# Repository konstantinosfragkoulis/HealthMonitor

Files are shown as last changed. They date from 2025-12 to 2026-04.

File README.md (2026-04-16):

# HealthMonitor 

Bare metal wearable for real-time Electrocardiogram (ECG), Seismocardiogram (SCG), and respiratory rate extraction.

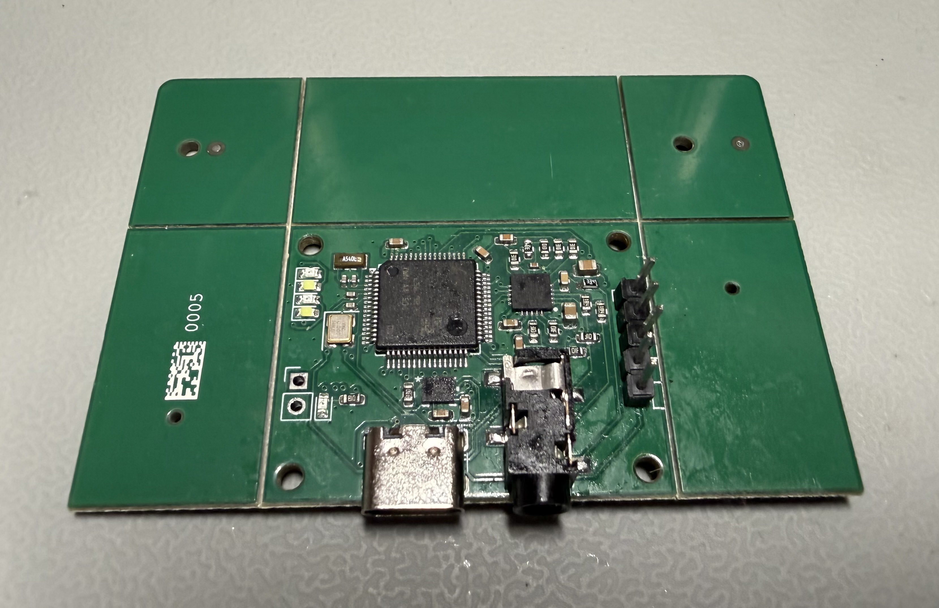
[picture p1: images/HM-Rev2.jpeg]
Health Monitor Rev2 PCB


**Core Stack:** STM32U5 (Cortex-M33) | ST1VAFE6AX (6-axis IMU) | AD8232 (ECG AFE)

## Architecture & DSP
To guarantee precise timing, the firmware relies entirely on hardware synchronization. The IMU's data-ready external interrupt triggers a simultaneous DMA transfer for both the SPI bus (IMU) and the ADC (ECG). This locks both data streams to a 480 Hz sample rate, eliminating software polling jitter.

The main loop runs three independent DSP pipelines on-device:

* **ECG (Pan-Tompkins++):** Bandpass -> derivative -> squaring -> flattop smoothing -> MWI. Uses adaptive thresholding with search-back for real-time R-peak detection [1].
* **SCG (Template Matching NCC):** Accel Z-axis (dorso-ventral) filtered at 7-30 Hz. Bootstraps a heartbeat template during the first 10s via a 4th-power envelope and pairwise NCC [2]. Runs a sliding normalized cross-correlation against the template for continuous AO detection. The template is double-buffered and refreshed every 60s.
* **Respiratory Rate:** Accel Z-axis LPF -> decimated 48:1 (to 10 Hz) -> bandpass 0.1-0.6 Hz. Fed into a 30-second autocorrelation window, outputting a new respiratory rate every 5 seconds.

HRV metrics (RMSSD, SDNN, pNN50, SD1, SD2) are calculated independently for both the ECG and SCG streams over a 60 second sliding window based on Task Force standards [3,4]. ECG and SCG reports are synchronized as the ECG trigger drives both computations simultaneously. Data is streamed to a host via a USB Virtual COM Port with CRC-32 integrity.

## Project Structure
* `/hardware/HM-Rev1`: First spin. **See `ERRATA.md`** (known routing/schematic flaw with the AD8232).
* `/hardware/HM-Rev2`: Fixed AD8232 layout, added USB-C, placed components on the bottom layer.
* `/fw`: STM32CubeIDE project, bare-metal C source, DSP logic, and TinyUSB stack.
* `/software`: Python telemetry parser and plotter.

## Roadmap
- [x] Hardware validation.
- [x] Synchronized IMU + ECG DMA capture.
- [x] ECG R-peak detection (Pan-Tompkins++).
- [x] SCG heartbeat detection (Template Matching NCC).
- [x] Real-time respiratory rate from chest-wall accelerometry.
- [x] On-device HRV metrics calculation.
- [x] USB CDC telemetry via TinyUSB.
- [x] SCG vs ECG HRV validation.
- [ ] Improve SCG RMSSD agreement
- [ ] Multi-axis respiratory fusion (PCA + gyro).

## SCG vs ECG HRV Validation

To validate the SCG pipeline, both streams are recorded simultaneously and HRV metrics are compared using Bland-Altman analysis, Pearson correlation, and ICC(2,1). Results from a 30 minute resting session (single subject, n=57 paired reports after 4 outliers removed via 3xIQR on RMSSD):

| Metric | Bias | 95% LOA | r | ICC(2,1) |
|--------|------|---------|---|----------|
| SDNN | -2.0 ms | [-6.0, +1.9] | 0.988 | 0.961 |
| SD2 | -0.9 ms | [-3.6, +1.9] | 0.996 | 0.994 |
| RMSSD | -6.3 ms | [-16.2, +3.5] | 0.378 | 0.175 |

SDNN and SD2 show excellent agreement. RMSSD underestimates ECG systematically. The SCG pipeline captures long term variability accurately but doesn't perform well with beat-to-beat variations.

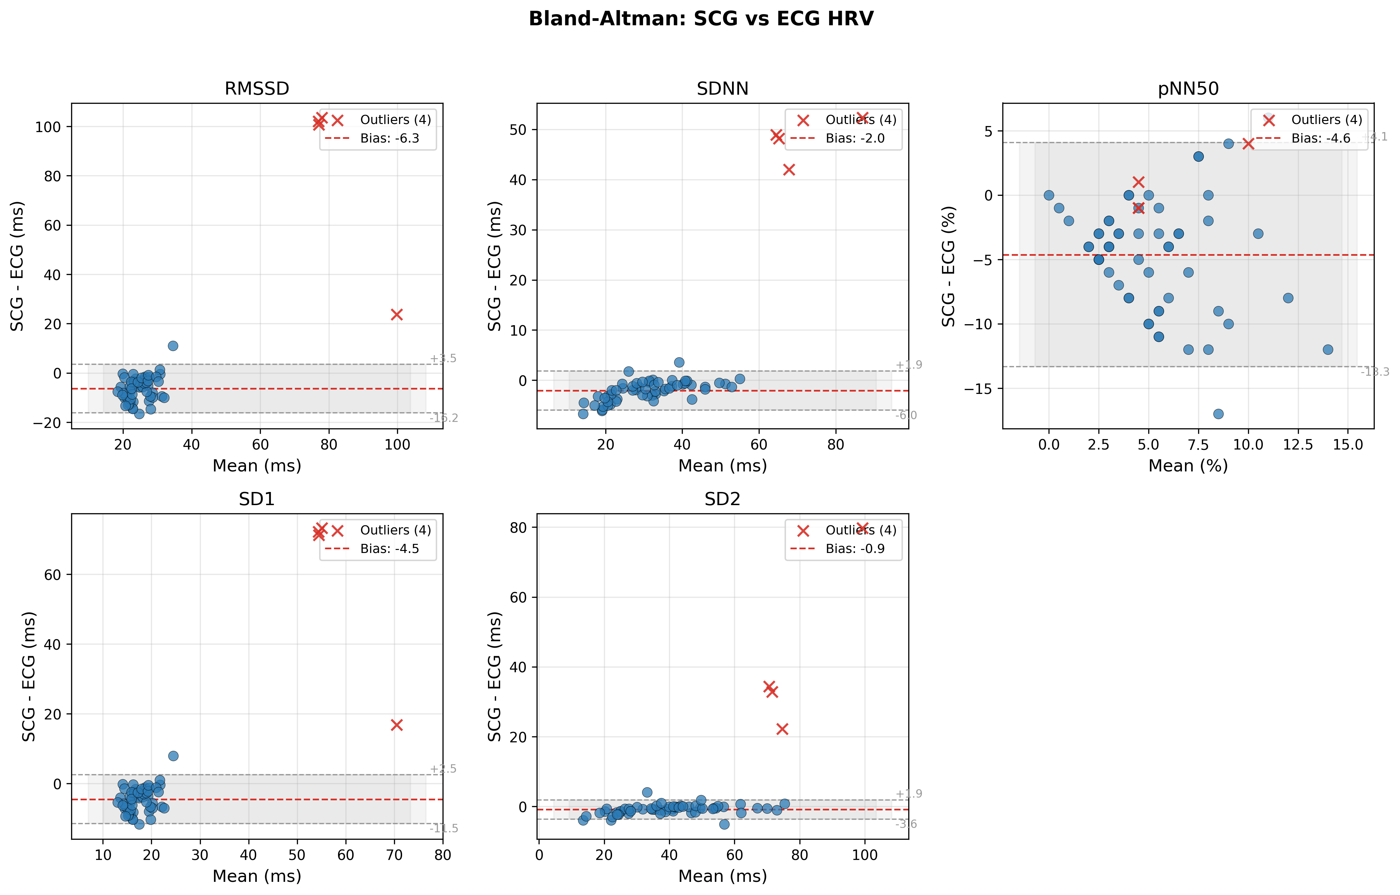
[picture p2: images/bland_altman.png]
Bland-Altman: SCG vs ECG HRV


The validation script reports both unfiltered and filtered results.
Run `python software/analyze.py <session_dir>` to produce the table and plots with data saved from the `software/monitor.py` script.

## Build Instructions
Compiled with **STM32CubeIDE**.
1. `git clone https://github.com/konstantinosfragkoulis/HealthMonitor.git`
2. Open STM32CubeIDE > `File > STM32 Project Create/Import > Import STM32 Project > STM32CubeMX/STM32CubeIDE Project`.
3. Point to the `/fw` directory.
4. Build (Release/Debug) and flash via ST-Link.

## Host Telemetry
The STM32 streams binary packets over USB CDC. Use the included Python script to plot sensor data in real time.

```bash
cd software
pip install pyserial numpy matplotlib # You might want to use a virtual environment for this

# Auto detect port
python monitor.py

# Manually select port
python monitor.py COM3         # Windows
python monitor.py /dev/ttyACM0 # Linux
```

## References
- USB stack powered by the open-source [TinyUSB](https://github.com/hathach/tinyusb) library (MIT License).

[1] M. N. Imtiaz and N. Khan, "Pan-Tompkins++: A Robust Approach to Detect R-peaks in ECG Signals," in *Proc. IEEE Int. Conf. Bioinformatics and Biomedicine (BIBM) Workshops*, 2022. [Online]. Available: https://arxiv.org/abs/2211.03171

[2] S. Parlato, J. Centracchio, D. Esposito, P. Bifulco, and E. Andreozzi, "Fully automated template matching method for ECG-free heartbeat detection in cardiomechanical signals," *Physical and Engineering Sciences in Medicine*, vol. 48, pp. 649-664, 2025.

[3] Task Force of the European Society of Cardiology and the North American Society of Pacing and Electrophysiology, "Heart rate variability: standards of measurement, physiological interpretation and clinical use," *Circulation*, vol. 93, pp. 1043-1065, 1996.

[4] F. Shaffer and J. P. Ginsberg, "An Overview of Heart Rate Variability Metrics and Norms," *Frontiers in Public Health*, vol. 5, 258, 2017.

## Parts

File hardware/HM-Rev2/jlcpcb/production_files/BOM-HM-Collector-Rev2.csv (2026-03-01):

Comment | Designator | Footprint | LCSC | Quantity
100k | R13 | R_0603_1608Metric | C25803 | 1
100n | C1,C12,C15,C22,C23,C29,C30,C31,C32,C33,C4,C5,C6,C8 | C_0603_1608Metric | C14663 | 14
10M | R10,R3,R4,R5,R9 | R_0603_1608Metric | C7250 | 5
10k | R1,R19,R2,R22 | R_0603_1608Metric | C25804 | 4
10u | C34,C35,C7,C9 | C_0805_2012Metric | C440198 | 4
12p | C16,C17 | C_0402_1005Metric | C1547 | 2
180k | R6,R7 | R_0603_1608Metric | C22827 | 2
18p | C18,C19 | C_0402_1005Metric | C1549 | 2
1M | R11,R12,R15,R20,R21 | R_0603_1608Metric | C22935 | 5
1k | R28,R29,R30,R31,R32 | R_0603_1608Metric | C21190 | 5
1n | C25 | C_0603_1608Metric | C1588 | 1
1u | C13,C14,C2,C20,C21,C3 | C_0603_1608Metric | C15849 | 6
2.2u | C10,C11 | C_0603_1608Metric | C23630 | 2
2.7n | C27 | C_0603_1608Metric | C1609 | 1
33 | R16,R17,R18,R23,R24,R25 | R_0603_1608Metric | C23140 | 6
4.7u | C24,C28 | C_0805_2012Metric | C1779 | 2
5.1k | R26,R27 | R_0603_1608Metric | C23186 | 2
6.8n | C26 | C_0402_1005Metric | C1542 | 1
AD8232ACPZ-R7 | IC2 | QFN50P400X400X80-21N-D | C43216 | 1
Crystal | Y2 | Crystal_SMD_3215-2Pin_3.2x1.5mm | C32346 | 1
Crystal_GND24 | Y1 | Crystal_SMD_3225-4Pin_3.2x2.5mm | C13738 | 1
D | D1,D2 | D_SOD-123 | C8598 | 2
LED | D3,D5,D7 | LED_0603_1608Metric | C2286 | 3
LED | D4,D6 | LED_0603_1608Metric | C2290 | 2
ST1VAFE6AXTR | U2 | LGA-14L_STM | C23536654 | 1
STM32U595RJTxQ | U1 | LQFP-64_10x10mm_P0.5mm | C27526235 | 1
TPS7A2028PDBVR | IC1,IC3 | SOT95P280X145-5N | C2862740 | 2
USB_C_Receptacle_USB2.0_16P | J3 | USB_C_Receptacle_GCT_USB4105-xx-A_16P_TopMnt_Horizontal | C709357 | 1

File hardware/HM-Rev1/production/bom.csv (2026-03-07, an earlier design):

Designator | Footprint | Quantity | Value | LCSC Part #
C1, C10, C11, C16, C18, C2, C20, C29, C3, C30, C35, C36, C37, C4, C5, C6, C7, C8, C9 | 0603 | 19 | 100nF
C12, C15 | 0805 | 2 | 10uF
C13, C14 | 0603 | 2 | 2.2uF
C17, C19, C25, C26, C27, C28 | 0603 | 6 | 1uF
C21, C22 | 0402 | 2 | 8pF
C23, C24 | 0402 | 2 | 6pF
C31 | 0805 | 1 | 4.7uF
C32 | 0603 | 1 | 1nF
C33 | 0402 | 1 | 6.8nF
C34 | 0402 | 1 | 2.7nF
D1, D2, D3, D4 | 0402 | 4 | LED
IC1, IC2 | SOT95P280X145-5N | 2 | TPS7A2028PDBVR
IC3 | QFN50P400X400X80-21N-D | 1 | AD8232ACPZ-R7
J1 | PinHeader_1x05_P2.54mm_Horizontal | 1 | Conn_01x05_Pin
J2 | SJ235813BSMTTR | 1 | SJ2-35813B-SMT-TR
L1 | 1008 | 1 | 2.2uH
R1, R2, R21, R22, R23, R24, R25, R26 | 0603 | 8 | 10kOhm
R10 | 0603 | 1 | 360kOhm
R11, R13, R15, R16, R17 | 0603 | 5 | 1MOhm
R12 | 0603 | 1 | 100kOhm
R14 | 0603 | 1 | 332kOhm
R18, R19, R20, R27, R28, R29 | 0402 | 6 | 33Ohm
R3, R4, R5, R8, R9 | 0603 | 5 | 10MOhm
R6, R7 | 0603 | 2 | 180kOhm
TP1, TP2 | PinHeader_1x01_P2.54mm_Vertical | 2 | TestPoint
U1 | LQFP-100_14x14mm_P0.5mm | 1 | STM32U5G9VJTxQ
U2 | LGA-14L_STM | 1 | ST1VAFE6AXTR
U3 | SOIC-8_5.3x5.3mm_P1.27mm | 1 | W25Q128JVS
Y1 | Crystal_SMD_3215-2Pin_3.2x1.5mm | 1 | 32.768kHz
Y2 | CX3225FB16000D0FZZH1 | 1 | CX3225FB16000D0FZZH1

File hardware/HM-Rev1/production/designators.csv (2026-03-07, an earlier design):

C1:1
C10:1
C11:1
C12:1
C13:1
C14:1
C15:1
C16:1
C17:1
C18:1
C19:1
C2:1
C20:1
C21:1
C22:1
C23:1
C24:1
C25:1
C26:1
C27:1
C28:1
C29:1
C3:1
C30:1
C31:1
C32:1
C33:1
C34:1
C35:1
C36:1
C37:1
C4:1
C5:1
C6:1
C7:1
C8:1
C9:1
D1:1
D2:1
D3:1
D4:1
IC1:1
IC2:1
IC3:1
J1:1
J2:1
JP1:1
L1:1
R1:1
R10:1
R11:1
R12:1
R13:1
R14:1
R15:1
R16:1
R17:1
R18:1
R19:1
R2:1
R20:1
R21:1
R22:1
R23:1
R24:1
R25:1
R26:1
R27:1
R28:1
R29:1
R3:1
R4:1
R5:1
R6:1
R7:1
R8:1
R9:1
TP1:1
TP2:1
U1:1
U2:1
U3:1
Y1:1
Y2:1

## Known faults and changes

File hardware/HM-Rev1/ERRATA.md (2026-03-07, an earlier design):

# HM-Rev1 Known Issues

**Note: This board was abandoned and never fully assembled**

## 1. AD8232 Incorrect Wiring
* One 4.7 uF capacitor is missing between IOUT and SW
* One resistor and one capacitor are wired incorrectly between REFIN and GND

This error was caught *before* testing the board, so the AD8232 was never tested. Most likely, the signal filtering would not have worked correctly. This is fixed in [HM-Rev2](../HM-Rev2).

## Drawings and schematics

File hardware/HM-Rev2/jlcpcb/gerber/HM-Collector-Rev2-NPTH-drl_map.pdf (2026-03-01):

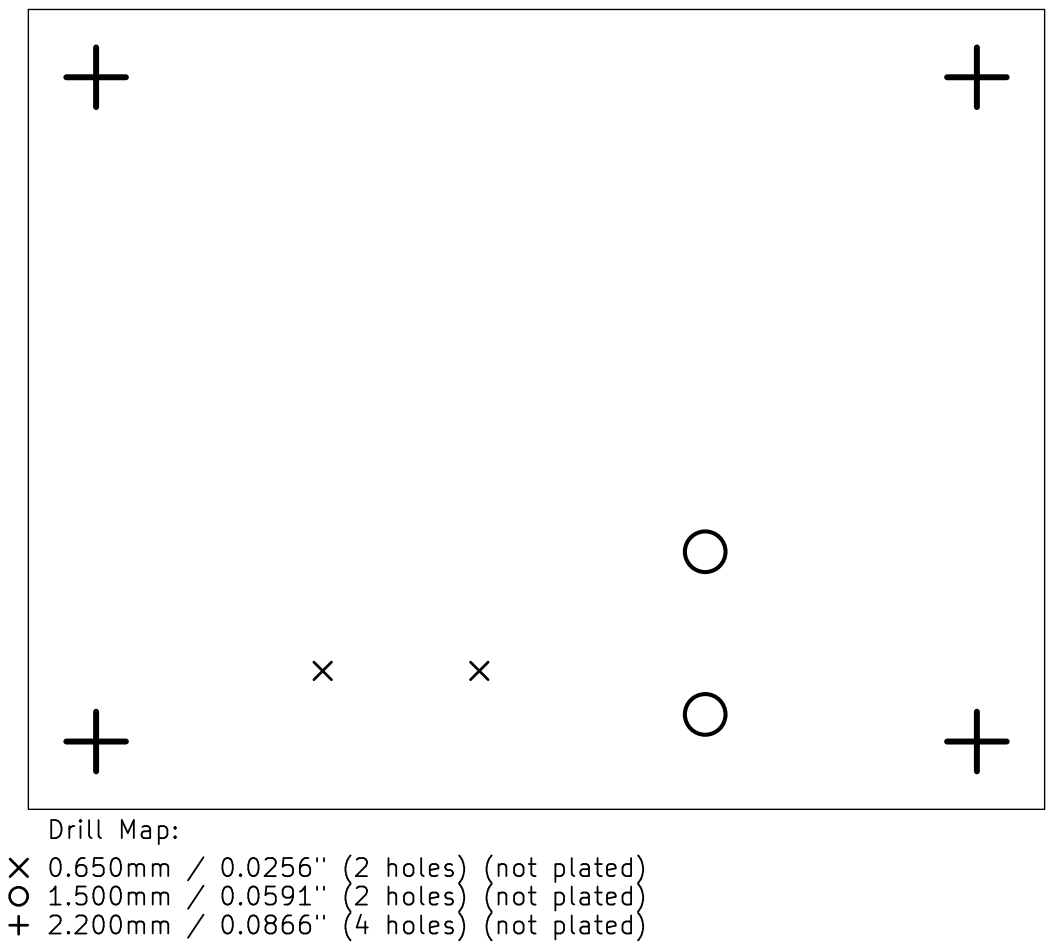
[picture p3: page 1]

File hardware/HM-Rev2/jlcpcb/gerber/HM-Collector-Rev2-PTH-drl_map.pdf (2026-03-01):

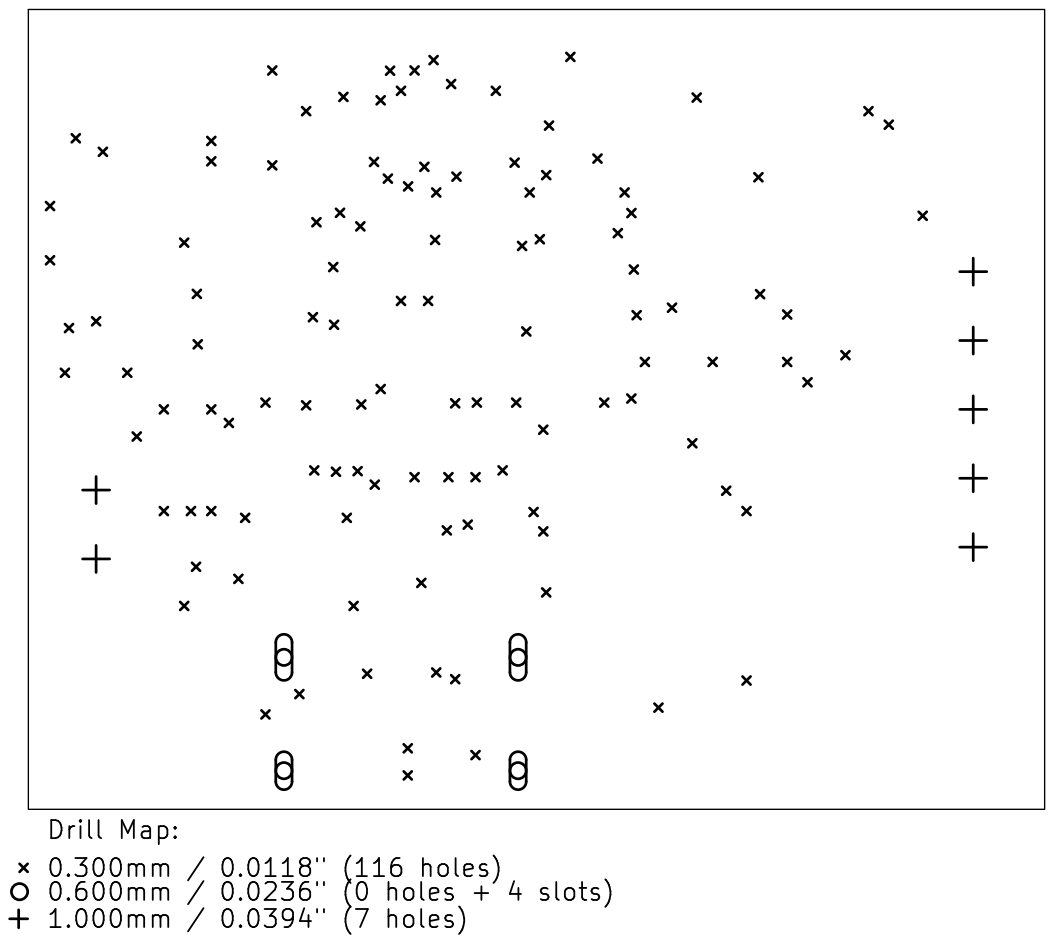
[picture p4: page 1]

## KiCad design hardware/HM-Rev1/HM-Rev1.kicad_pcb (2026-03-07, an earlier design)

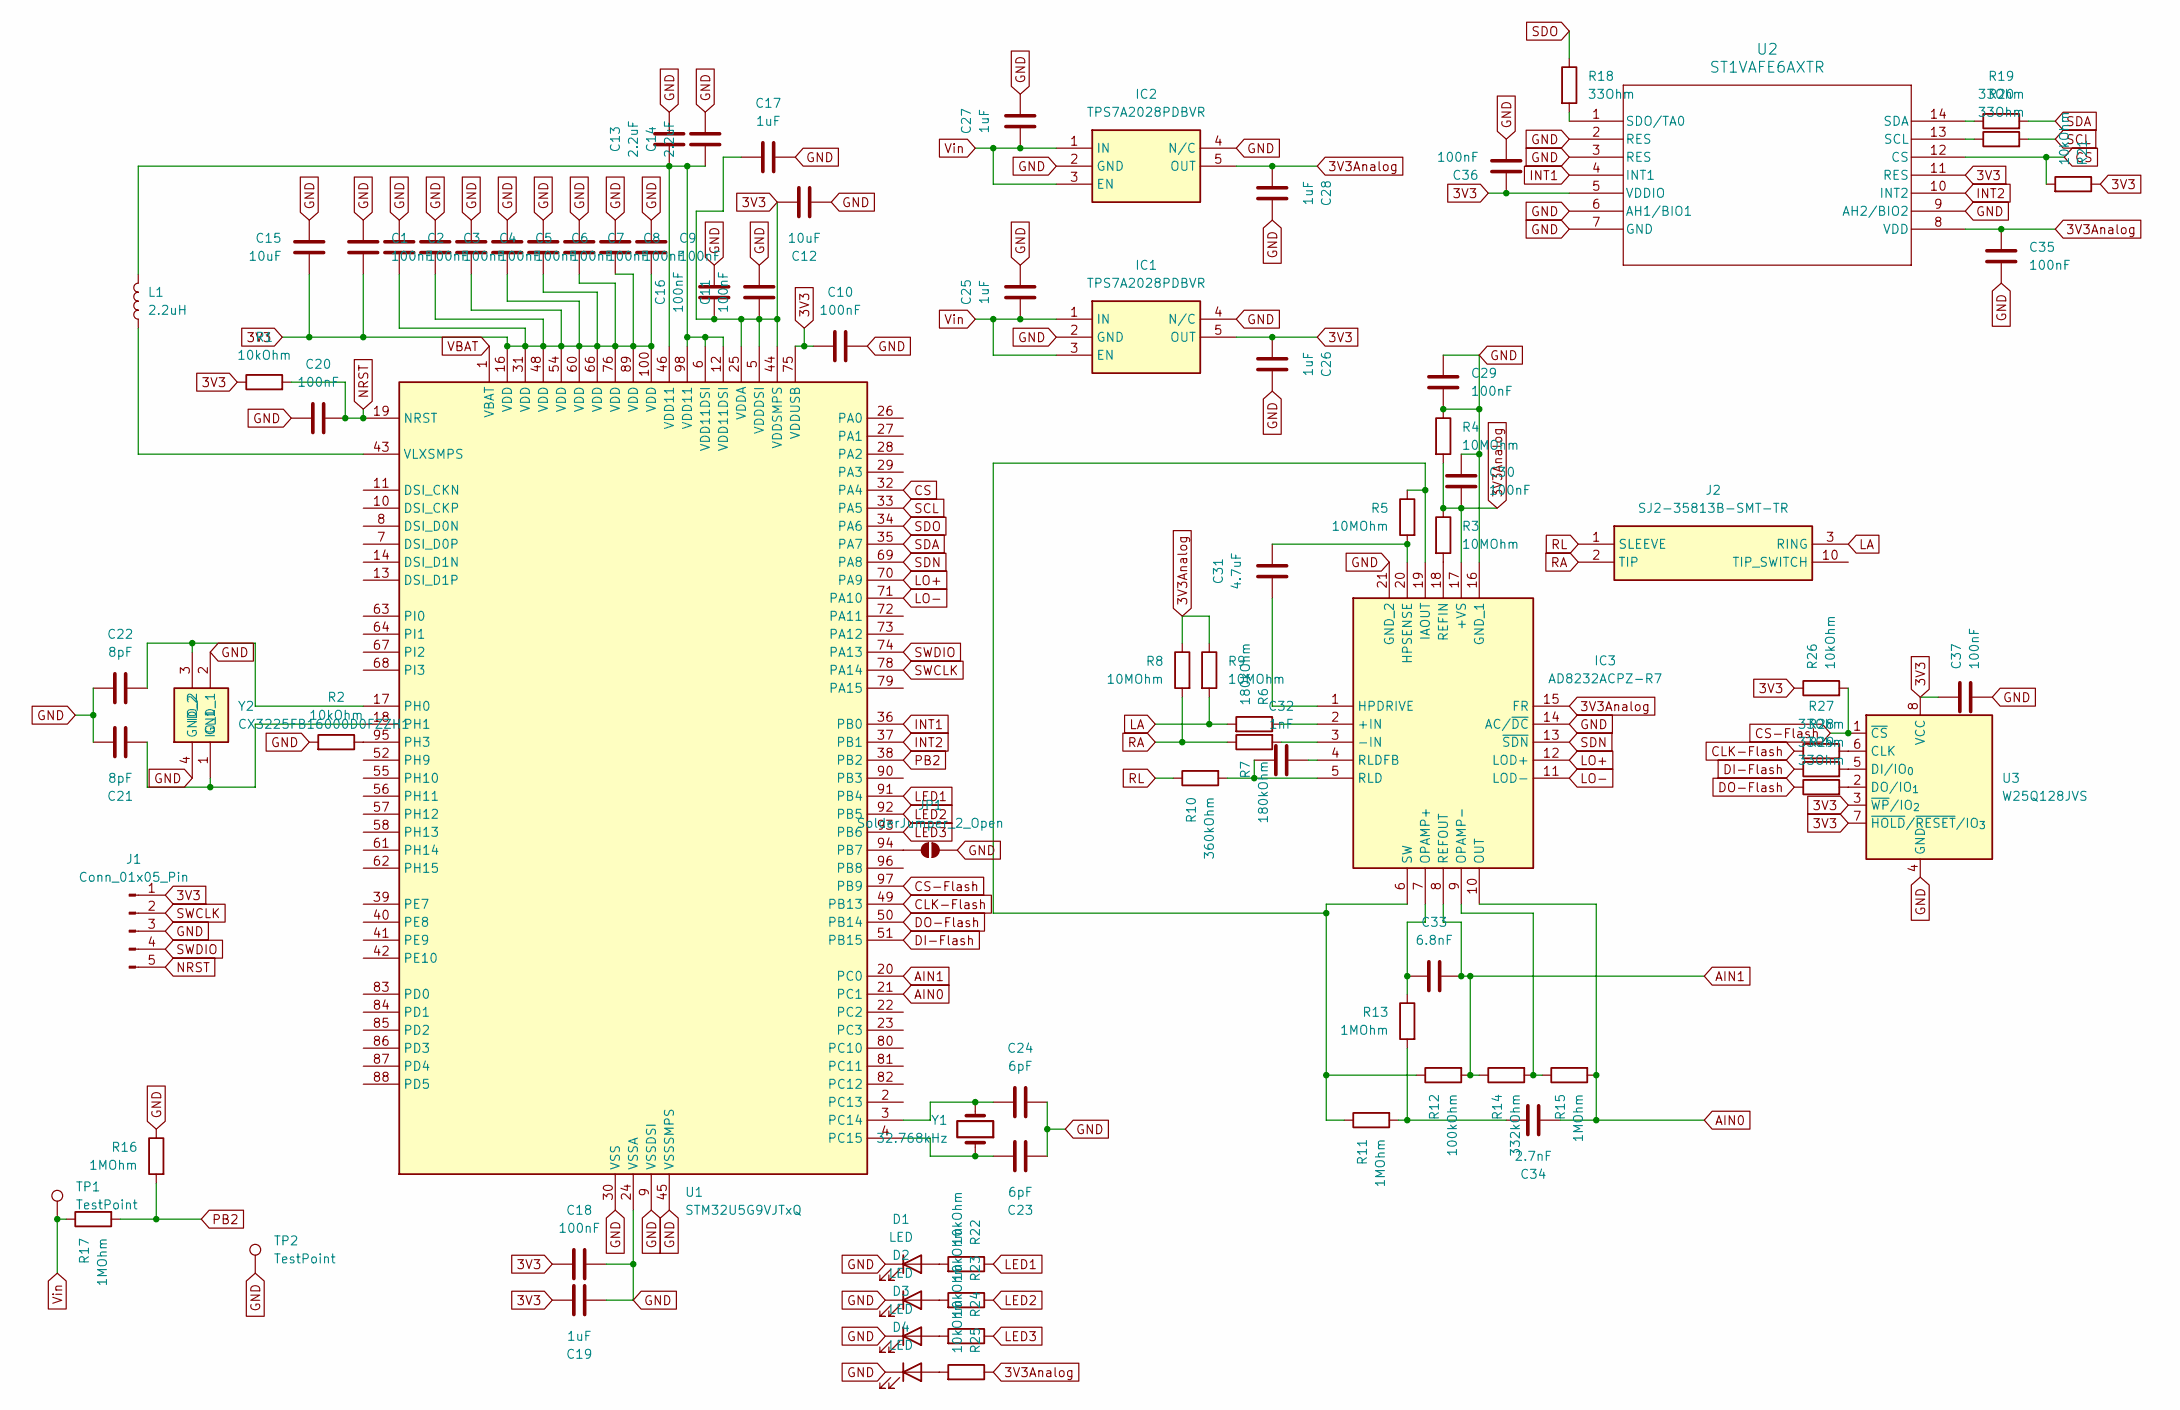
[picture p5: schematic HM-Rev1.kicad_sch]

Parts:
C1, C2, C3, C4, C5, C6, C7, C8, C9, C10, C11, C16, C18, C20, C29, C30, C35, C36, C37: 100nF; C_0603_1608Metric
C12, C15: 10uF; C_0805_2012Metric
C13, C14: 2.2uF; C_0603_1608Metric
C17, C19, C25, C26, C27, C28: 1uF; C_0603_1608Metric
C21, C22: 8pF; C_0402_1005Metric
C23, C24: 6pF; C_0402_1005Metric
C31: 4.7uF; C_0805_2012Metric
C32: 1nF; C_0603_1608Metric
C33: 6.8nF; C_0402_1005Metric
C34: 2.7nF; C_0402_1005Metric
D1, D2, D3, D4: LED; LED_0402_1005Metric_Pad0.77x0.64mm_HandSolder
IC1, IC2: TPS7A2028PDBVR; SOT95P280X145-5N; Mouser Part Number 595-TPS7A2028PDBVR
IC3: AD8232ACPZ-R7; QFN50P400X400X80-21N-D; Mouser Part Number 584-AD8232ACPZ-R7
J1: Conn_01x05_Pin; PinHeader_1x05_P2.54mm_Horizontal
J2: SJ2-35813B-SMT-TR; SJ235813BSMTTR; Mouser Part Number 490-SJ2-35813BSMT-TR
JP1: SolderJumper_2_Open; SolderJumper-2_P1.3mm_Open_Pad1.0x1.5mm
L1: 2.2uH; L_1008_2520Metric
R1, R2, R21, R22, R23, R24, R25, R26: 10kOhm; R_0603_1608Metric
R3, R4, R5, R8, R9: 10MOhm; R_0603_1608Metric
R6, R7: 180kOhm; R_0603_1608Metric
R10: 360kOhm; R_0603_1608Metric
R11, R13, R15, R16, R17: 1MOhm; R_0603_1608Metric
R12: 100kOhm; R_0603_1608Metric
R14: 332kOhm; R_0603_1608Metric
R18, R19, R20, R27, R28, R29: 33Ohm; R_0402_1005Metric
TP1, TP2: TestPoint; PinHeader_1x01_P2.54mm_Vertical
U1: STM32U5G9VJTxQ; LQFP-100_14x14mm_P0.5mm
U2: ST1VAFE6AXTR; LGA-14L_STM
U3: W25Q128JVS; SOIC-8_5.3x5.3mm_P1.27mm
Y1: 32.768kHz; Crystal_SMD_3215-2Pin_3.2x1.5mm
Y2: CX3225FB16000D0FZZH1; Manufacturer_Part_Number CX3225FB16000D0FZZH1

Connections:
3V3: C1.2, C2.2, C3.2, C4.2, C5.2, C6.2, C7.2, C8.2, C9.2, C10.1, C11.1, C12.1, C15.2, C16.1, C17.1, C18.2, C19.1, C26.1, C36.1, C37.1, IC1.5 (OUT), J1.1, R1.1, R21.1, R26.1, U1.5 (VDDDSI), U1.16 (VDD), U1.25 (VDDA), U1.31 (VDD), U1.44 (VDDSMPS), U1.48 (VDD), U1.54 (VDD), U1.60 (VDD), U1.66 (VDD), U1.75 (VDDUSB), U1.76 (VDD), U1.89 (VDD), U1.100 (VDD), U2.5 (VDDIO), U2.11 (RES), U3.3 (~WP/IO_{2}), U3.7 (~HOLD/~RESET/IO_{3}), U3.8 (VCC)
3V3Analog: C28.1, C30.1, C35.1, IC2.5 (OUT), IC3.15 (FR), IC3.17 (+VS), R3.1, R4.2, R8.1, R9.1, R25.1, U2.8 (VDD)
AIN0: C34.2, IC3.10 (OUT), R15.2, U1.21 (PC1)
AIN1: C33.1, IC3.8 (REFOUT), R12.2, R14.1, U1.20 (PC0)
CLK-Flash: R27.1, U1.49 (PB13)
CS: R21.2, U1.32 (PA4), U2.12 (CS)
CS-Flash: R26.2, U1.97 (PB9), U3.1 (~CS)
DI-Flash: R28.1, U1.51 (PB15)
DO-Flash: R29.1, U1.50 (PB14)
GND: C1.1, C2.1, C3.1, C4.1, C5.1, C6.1, C7.1, C8.1, C9.1, C10.2, C11.2, C12.2, C13.2, C14.2, C15.1, C16.2, C17.2, C18.1, C19.2, C20.1, C21.1, C22.2, C23.2, C24.1, C25.2, C26.2, C27.2, C28.2, C29.1, C29.2, C30.2, C35.2, C36.2, C37.2, D1.1 (K), D2.1 (K), D3.1 (K), D4.1 (K), IC1.2 (GND), IC1.4 (N/C), IC2.2 (GND), IC2.4 (N/C), IC3.14 (AC/~DC), IC3.16 (GND_1), IC3.21 (GND_2), J1.3, JP1.2 (B), R2.2, R4.1, R16.1, TP2.1, U1.9 (VSSDSI), U1.15 (VSSDSI), U1.24 (VSSA), U1.30 (VSS), U1.45 (VSSSMPS), U1.47 (VSS), U1.53 (VSS), U1.59 (VSS), U1.65 (VSS), U1.77 (VSS), U1.99 (VSS), U2.2 (RES), U2.3 (RES), U2.6 (AH1/BIO1), U2.7 (GND), U2.9 (AH2/BIO2), U3.4 (GND), Y2.2 (GND_1), Y2.4 (GND_2)
INT1: U1.36 (PB0), U2.4 (INT1)
INT2: U1.37 (PB1), U2.10 (INT2)
LA: J2.3 (RING), R6.2, R9.2
LED1: R22.1, U1.91 (PB4)
LED2: R23.1, U1.92 (PB5)
LED3: R24.1, U1.93 (PB6)
LO+: IC3.12 (LOD+), U1.70 (PA9)
LO-: IC3.11 (LOD-), U1.71 (PA10)
NRST: C20.2, J1.5, R1.2, U1.19 (NRST)
unnamed: C13.1, C14.1, L1.2, U1.6 (VDD11DSI), U1.12 (VDD11DSI), U1.46 (VDD11), U1.98 (VDD11)
unnamed: C34.1, R11.2, R13.2
unnamed: D1.2 (A), R22.2
unnamed: D2.2 (A), R23.2
unnamed: D3.2 (A), R24.2
unnamed: D4.2 (A), R25.2
unnamed: IC3.2 (+IN), R6.1
unnamed: IC3.3 (-IN), R7.2
unnamed: C31.1, IC3.1 (HPDRIVE)
unnamed: C31.2, IC3.20 (HPSENSE), R5.2
unnamed: IC3.6 (SW), IC3.19 (IAOUT), R5.1, R11.1, R12.1
unnamed: C33.2, IC3.7 (OPAMP+), R13.1
unnamed: IC3.9 (OPAMP-), R14.2, R15.1
unnamed: IC3.18 (REFIN), R3.2
unnamed: C32.2, IC3.5 (RLD), R10.2
unnamed: C32.1, IC3.4 (RLDFB)
unnamed: JP1.1 (A), U1.94 (PB7)
unnamed: C24.2, U1.3 (PC14), Y1.2
unnamed: C23.1, U1.4 (PC15), Y1.1
unnamed: C22.1, U1.17 (PH0), Y2.3 (IO_2)
unnamed: C21.2, U1.18 (PH1), Y2.1 (IO_1)
unnamed: R2.1, U1.95 (PH3)
unnamed: L1.1, U1.43 (VLXSMPS)
unnamed: R20.1, U2.13 (SCL)
unnamed: R19.1, U2.14 (SDA)
unnamed: R18.2, U2.1 (SDO/TA0)
unnamed: R27.2, U3.6 (CLK)
unnamed: R28.2, U3.5 (DI/IO_{0})
unnamed: R29.2, U3.2 (DO/IO_{1})
PB2: R16.2, R17.2, U1.38 (PB2)
RA: J2.2 (TIP), R7.1, R8.2
RL: J2.1 (SLEEVE), R10.1
SCL: R20.2, U1.33 (PA5)
SDA: R19.2, U1.35 (PA7)
SDN: IC3.13 (~SDN), U1.69 (PA8)
SDO: R18.1, U1.34 (PA6)
SWCLK: J1.2, U1.78 (PA14)
SWDIO: J1.4, U1.74 (PA13)
VBAT: U1.1 (VBAT)
Vin: C25.1, C27.1, IC1.1 (IN), IC1.3 (EN), IC2.1 (IN), IC2.3 (EN), R17.1, TP1.1

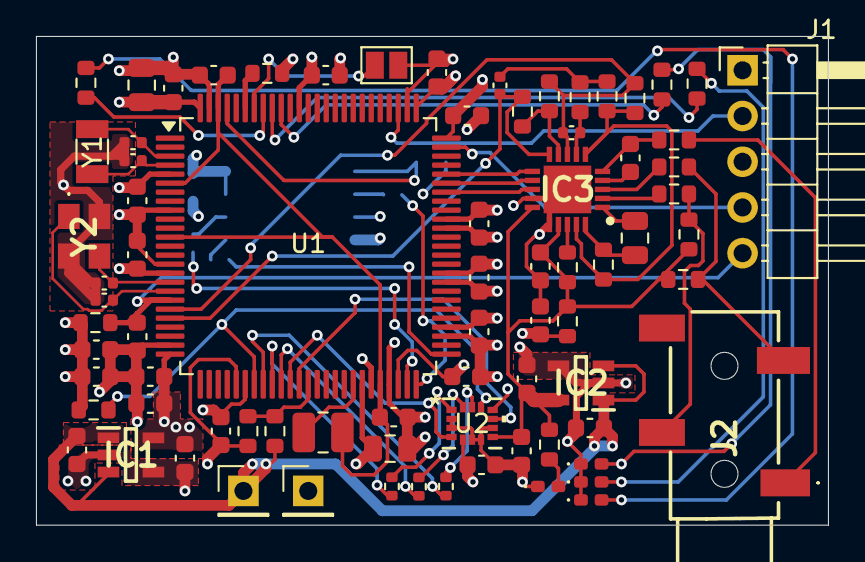
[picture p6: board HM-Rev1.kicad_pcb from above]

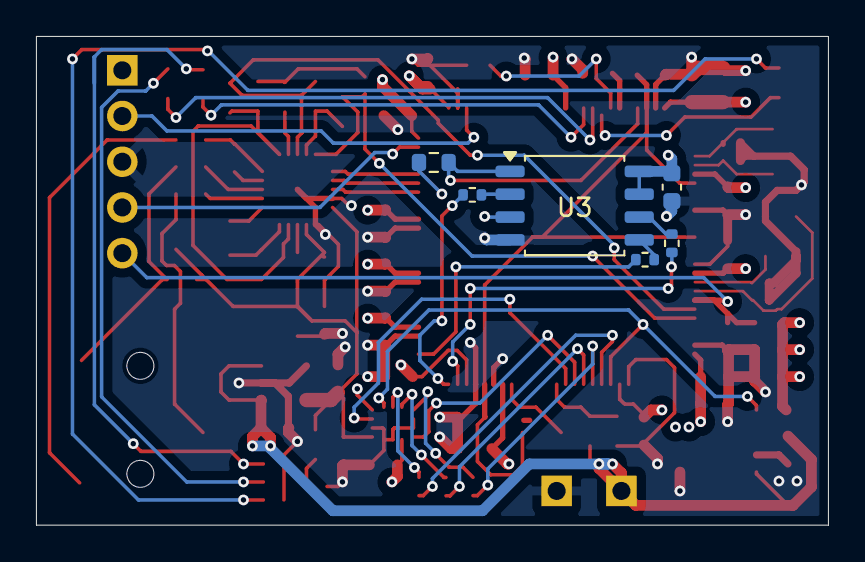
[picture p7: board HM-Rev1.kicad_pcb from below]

Board: 4 copper layers, 44.0 x 27.2 mm, 84 parts (6 on the bottom side), 58 nets.

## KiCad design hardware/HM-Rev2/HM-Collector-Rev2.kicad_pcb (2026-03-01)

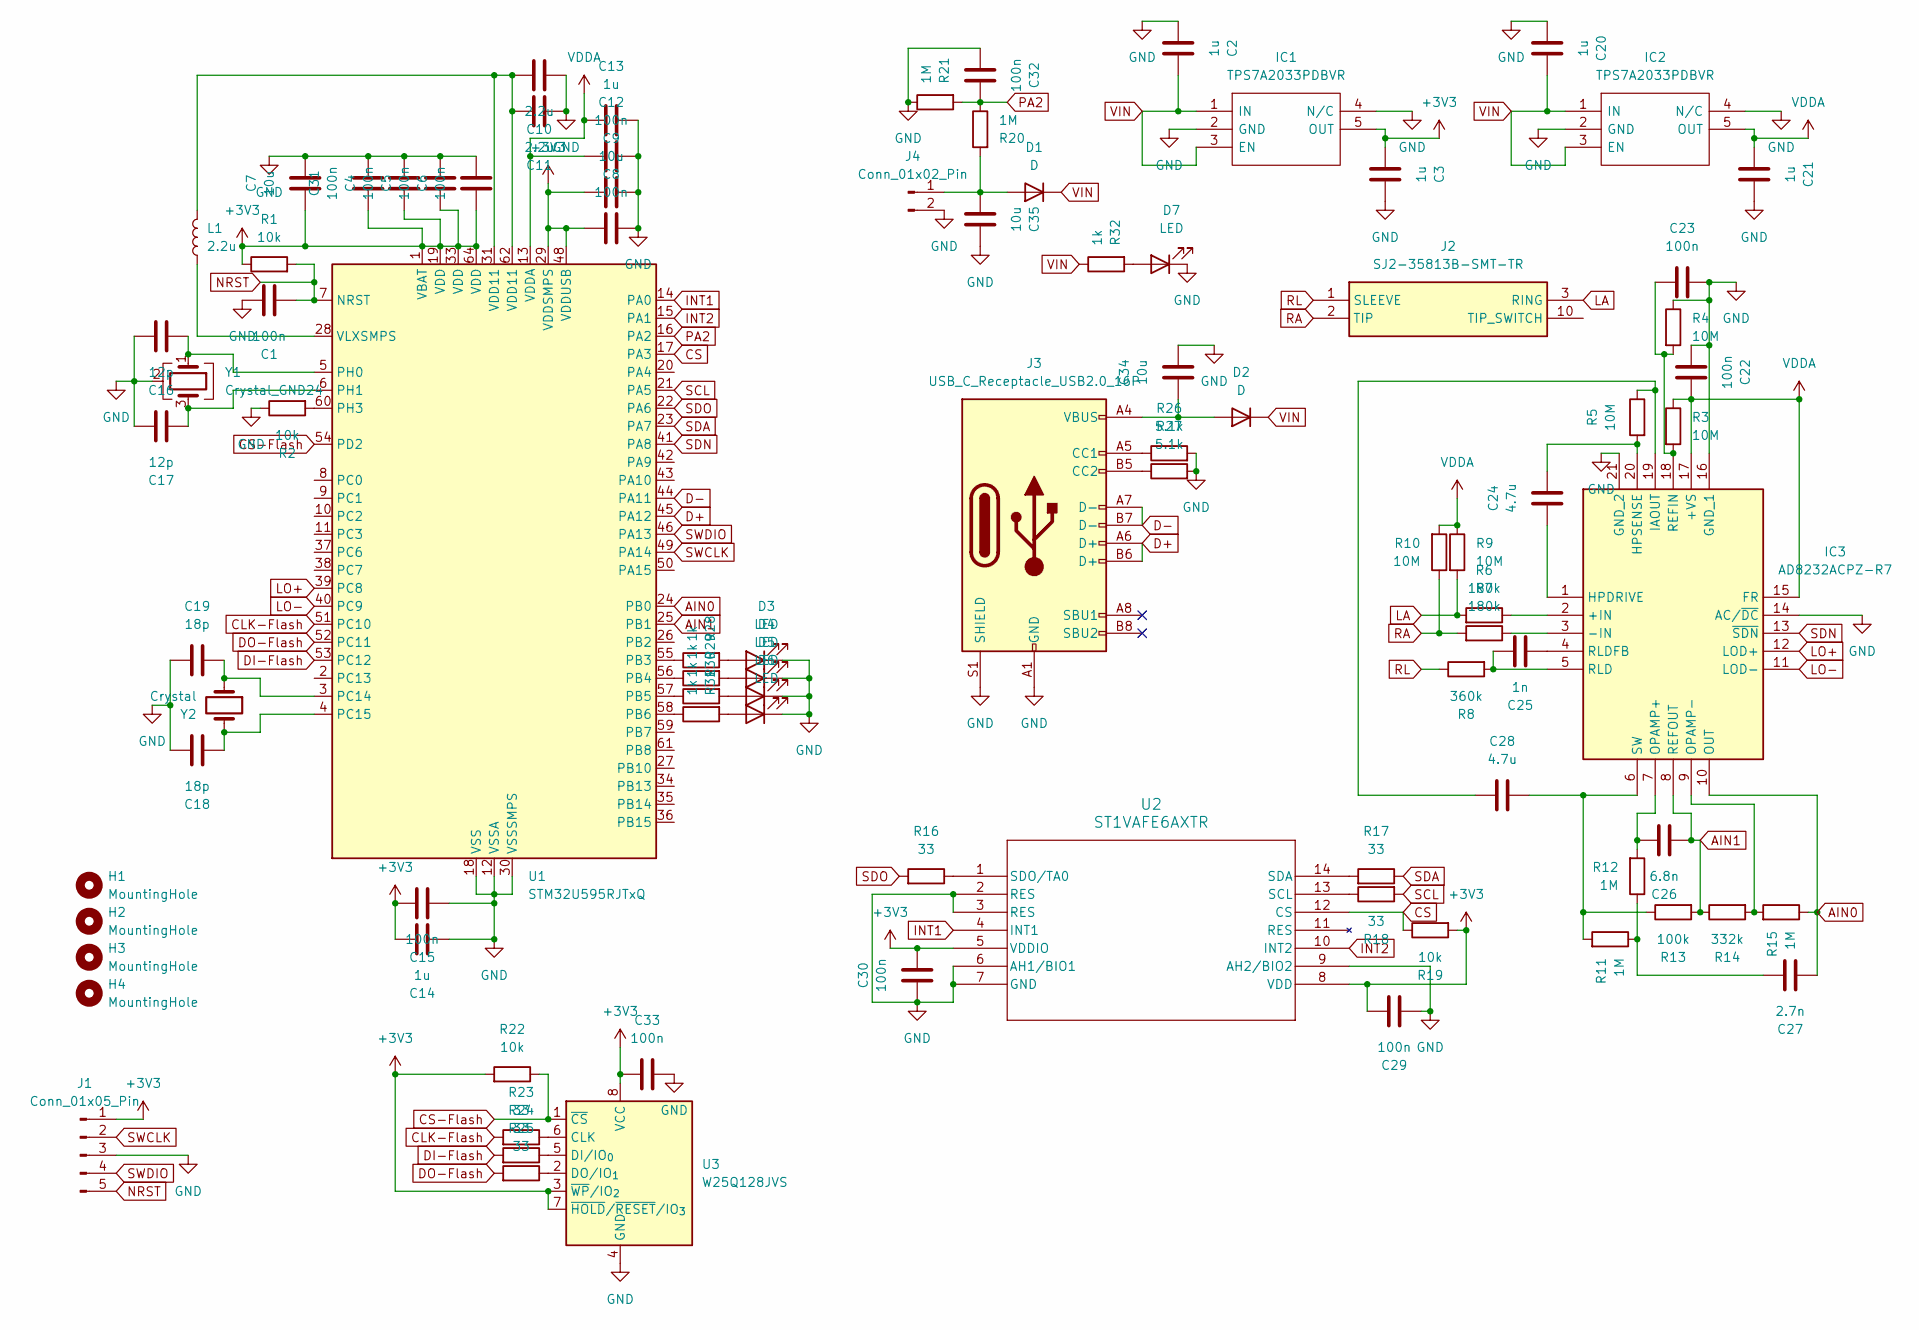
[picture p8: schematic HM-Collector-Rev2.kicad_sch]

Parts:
C1, C4, C5, C6, C8, C12, C15, C22, C23, C29, C30, C31, C32, C33: 100n; C_0603_1608Metric
C2, C3, C13, C14, C20, C21: 1u; C_0603_1608Metric
C7, C9, C34, C35: 10u; C_0805_2012Metric
C10, C11: 2.2u; C_0603_1608Metric
C16, C17: 12p; C_0402_1005Metric
C18, C19: 18p; C_0402_1005Metric
C24, C28: 4.7u; C_0805_2012Metric
C25: 1n; C_0603_1608Metric
C26: 6.8n; C_0402_1005Metric
C27: 2.7n; C_0603_1608Metric
D1, D2: D; D_SOD-123
D3, D4, D5, D6, D7: LED; LED_0603_1608Metric
H1, H2, H3, H4: MountingHole; MountingHole_2.2mm_M2
IC1, IC2: TPS7A2033PDBVR; SOT95P280X145-5N; Manufacturer_Part_Number TPS7A2033PDBVR; Mouser Part Number 595-TPS7A2033PDBVR
IC3: AD8232ACPZ-R7; QFN50P400X400X80-21N-D; Mouser Part Number 584-AD8232ACPZ-R7
J1: Conn_01x05_Pin; PinHeader_1x05_P2.54mm_Horizontal
J2: SJ2-35813B-SMT-TR; SJ235813BSMTTR; Mouser Part Number 490-SJ2-35813BSMT-TR
J3: USB_C_Receptacle_USB2.0_16P; USB_C_Receptacle_GCT_USB4105-xx-A_16P_TopMnt_Horizontal
J4: Conn_01x02_Pin; PinHeader_1x02_P2.54mm_Vertical
L1: 2.2u; L_1008_2520Metric
R1, R2, R19, R22: 10k; R_0603_1608Metric
R3, R4, R5, R9, R10: 10M; R_0603_1608Metric
R6, R7: 180k; R_0603_1608Metric
R8: 360k; R_0603_1608Metric
R11, R12, R15, R20, R21: 1M; R_0603_1608Metric
R13: 100k; R_0603_1608Metric
R14: 332k; R_0603_1608Metric
R16, R17, R18, R23, R24, R25: 33; R_0603_1608Metric
R26, R27: 5.1k; R_0603_1608Metric
R28, R29, R30, R31, R32: 1k; R_0603_1608Metric
U1: STM32U595RJTxQ; LQFP-64_10x10mm_P0.5mm
U2: ST1VAFE6AXTR; LGA-14L_STM
U3: W25Q128JVS; SOIC-8_5.3x5.3mm_P1.27mm
Y1: Crystal_GND24; Crystal_SMD_3225-4Pin_3.2x2.5mm
Y2: Crystal; Crystal_SMD_3215-2Pin_3.2x1.5mm

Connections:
+3V3: C3.2, C4.2, C5.2, C6.2, C7.2, C8.2, C9.2, C14.2, C15.1, C29.1, C30.1, C31.2, C33.2, IC1.5 (OUT), J1.1, R1.1, R19.2, R22.2, U1.1 (VBAT), U1.19 (VDD), U1.29 (VDDSMPS), U1.33 (VDD), U1.48 (VDDUSB), U1.64 (VDD), U2.5 (VDDIO), U2.8 (VDD), U3.3 (~WP/IO_{2}), U3.7 (~HOLD/~RESET/IO_{3}), U3.8 (VCC)
AIN0: C27.2, IC3.10 (OUT), R15.1, U1.24 (PB0)
AIN1: C26.2, IC3.8 (REFOUT), R13.2, R14.1, U1.25 (PB1)
CLK-Flash: R23.2, U1.51 (PC10)
CS: R19.1, U1.17 (PA3), U2.12 (CS)
CS-Flash: R22.1, U1.54 (PD2), U3.1 (~CS)
D+: J3.A6 (D+), J3.B6 (D+), U1.45 (PA12)
D-: J3.A7 (D-), J3.B7 (D-), U1.44 (PA11)
DI-Flash: R24.2, U1.53 (PC12)
DO-Flash: R25.2, U1.52 (PC11)
GND: C1.1, C2.2, C3.1, C4.1, C5.1, C6.1, C7.1, C8.1, C9.1, C10.1, C11.1, C12.1, C13.2, C14.1, C15.2, C16.1, C17.1, C18.1, C19.2, C20.2, C21.1, C22.2, C23.1, C29.2, C30.2, C31.1, C32.2, C33.1, C34.1, C35.1, D3.1 (K), D4.1 (K), D5.1 (K), D6.1 (K), D7.1 (K), IC1.2 (GND), IC1.4 (N/C), IC2.2 (GND), IC2.4 (N/C), IC3.14 (AC/~DC), IC3.16 (GND_1), IC3.21 (GND_2), J1.3, J3.A1 (GND), J3.A12 (GND), J3.B1 (GND), J3.B12 (GND), J3.S1 (SHIELD), J4.2, R2.1, R4.1, R21.1, R26.2, R27.2, U1.12 (VSSA), U1.18 (VSS), U1.30 (VSSSMPS), U1.32 (VSS), U1.47 (VSS), U1.63 (VSS), U2.2 (RES), U2.3 (RES), U2.6 (AH1/BIO1), U2.7 (GND), U2.9 (AH2/BIO2), U3.4 (GND), Y1.2 (G), Y1.4 (G)
INT1: U1.14 (PA0), U2.4 (INT1)
INT2: U1.15 (PA1), U2.10 (INT2)
LA: J2.3 (RING), R6.2, R9.2
LO+: IC3.12 (LOD+), U1.39 (PC8)
LO-: IC3.11 (LOD-), U1.40 (PC9)
NRST: C1.2, J1.5, R1.2, U1.7 (NRST)
unnamed: C10.2, C11.2, L1.2, U1.31 (VDD11), U1.62 (VDD11)
unnamed: C27.1, R11.1, R12.1
unnamed: C35.2, D1.2 (A), J4.1, R20.2
unnamed: C34.2, D2.2 (A), J3.A4 (VBUS), J3.A9 (VBUS), J3.B4 (VBUS), J3.B9 (VBUS)
unnamed: D3.2 (A), R28.2
unnamed: D4.2 (A), R29.2
unnamed: D5.2 (A), R30.2
unnamed: D6.2 (A), R31.2
unnamed: D7.2 (A), R32.2
unnamed: IC3.2 (+IN), R6.1
unnamed: IC3.3 (-IN), R7.1
unnamed: C24.2, IC3.1 (HPDRIVE)
unnamed: C24.1, IC3.20 (HPSENSE), R5.2
unnamed: C28.2, IC3.19 (IAOUT), R5.1
unnamed: C26.1, IC3.7 (OPAMP+), R12.2
unnamed: IC3.9 (OPAMP-), R14.2, R15.2
unnamed: C23.2, IC3.18 (REFIN), R3.2, R4.2
unnamed: C25.1, IC3.5 (RLD), R8.2
unnamed: C25.2, IC3.4 (RLDFB)
unnamed: C28.1, IC3.6 (SW), R11.2, R13.1
unnamed: J3.A5 (CC1), R26.1
unnamed: J3.B5 (CC2), R27.1
unnamed: R28.1, U1.55 (PB3)
unnamed: R29.1, U1.56 (PB4)
unnamed: R30.1, U1.57 (PB5)
unnamed: R31.1, U1.58 (PB6)
unnamed: C19.1, U1.3 (PC14), Y2.1
unnamed: C18.2, U1.4 (PC15), Y2.2
unnamed: C16.2, U1.5 (PH0), Y1.1
unnamed: C17.2, U1.6 (PH1), Y1.3
unnamed: R2.2, U1.60 (PH3)
unnamed: L1.1, U1.28 (VLXSMPS)
unnamed: R18.1, U2.13 (SCL)
unnamed: R17.2, U2.14 (SDA)
unnamed: R16.1, U2.1 (SDO/TA0)
unnamed: R23.1, U3.6 (CLK)
unnamed: R24.1, U3.5 (DI/IO_{0})
unnamed: R25.1, U3.2 (DO/IO_{1})
PA2: C32.1, R20.1, R21.2, U1.16 (PA2)
RA: J2.2 (TIP), R7.2, R10.1
RL: J2.1 (SLEEVE), R8.1
SCL: R18.2, U1.21 (PA5)
SDA: R17.1, U1.23 (PA7)
SDN: IC3.13 (~SDN), U1.41 (PA8)
SDO: R16.2, U1.22 (PA6)
SWCLK: J1.2, U1.49 (PA14)
SWDIO: J1.4, U1.46 (PA13)
VDDA: C12.2, C13.1, C21.2, C22.1, IC2.5 (OUT), IC3.15 (FR), IC3.17 (+VS), R3.1, R9.1, R10.2, U1.13 (VDDA)
VIN: C2.1, C20.1, D1.1 (K), D2.1 (K), IC1.1 (IN), IC1.3 (EN), IC2.1 (IN), IC2.3 (EN), R32.1

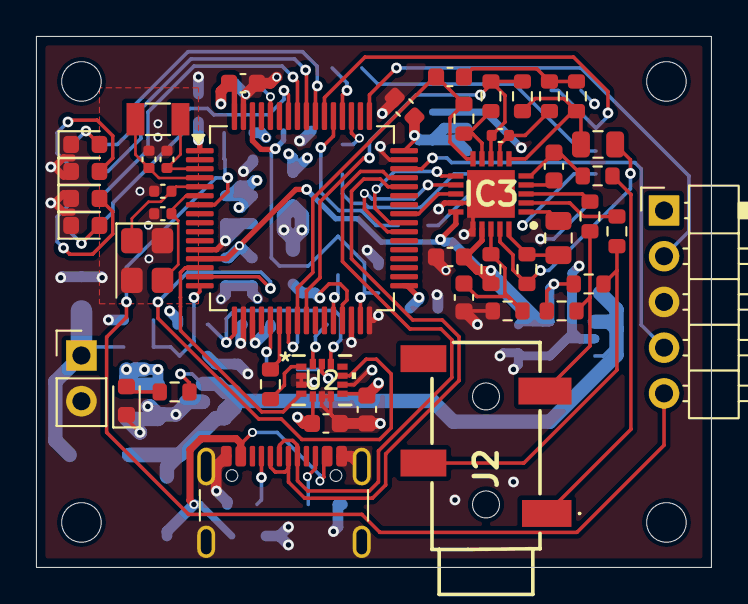
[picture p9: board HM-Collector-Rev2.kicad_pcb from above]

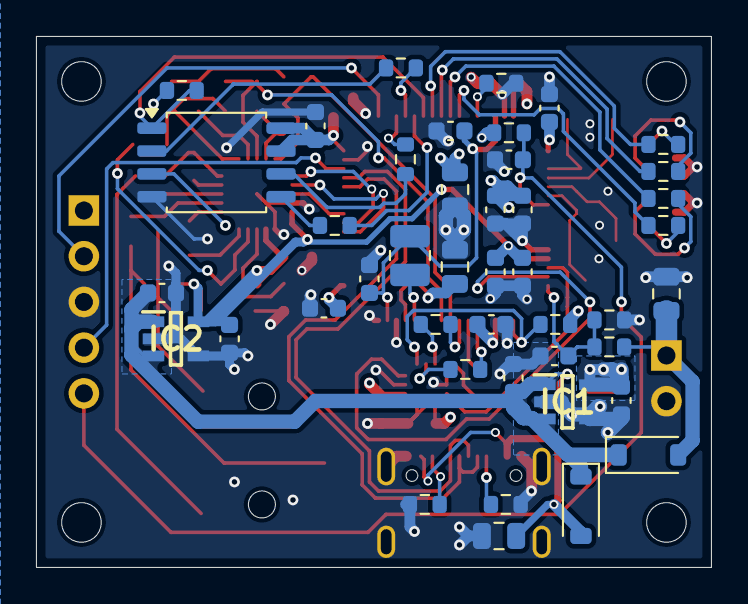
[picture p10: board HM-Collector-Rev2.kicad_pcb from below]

Board: 4 copper layers, 37.5 x 29.5 mm, 91 parts (43 on the bottom side), 66 nets.

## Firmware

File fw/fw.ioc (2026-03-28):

#MicroXplorer Configuration settings - do not modify
ADC1.Channel-1\#ChannelRegularConversion=ADC_CHANNEL_7
ADC1.Channel-2\#ChannelRegularConversion=ADC_CHANNEL_15
ADC1.Channel-3\#ChannelRegularConversion=ADC_CHANNEL_16
ADC1.ClockPrescaler=ADC_CLOCK_ASYNC_DIV2
ADC1.ConversionDataManagement=ADC_CONVERSIONDATA_DMA_ONESHOT
ADC1.DMAContinuousRequests=ENABLE
ADC1.ExternalTrigConv=ADC_SOFTWARE_START
ADC1.IPParameters=Rank-1\#ChannelRegularConversion,Channel-1\#ChannelRegularConversion,SamplingTime-1\#ChannelRegularConversion,OffsetNumber-1\#ChannelRegularConversion,MonitoredBy-1\#ChannelRegularConversion,NbrOfConversionFlag,ClockPrescaler,Rank-2\#ChannelRegularConversion,Channel-2\#ChannelRegularConversion,SamplingTime-2\#ChannelRegularConversion,OffsetNumber-2\#ChannelRegularConversion,MonitoredBy-2\#ChannelRegularConversion,Rank-3\#ChannelRegularConversion,Channel-3\#ChannelRegularConversion,SamplingTime-3\#ChannelRegularConversion,OffsetNumber-3\#ChannelRegularConversion,MonitoredBy-3\#ChannelRegularConversion,NbrOfConversion,ExternalTrigConv,master,DMAContinuousRequests,ConversionDataManagement
ADC1.MonitoredBy-1\#ChannelRegularConversion=__NULL
ADC1.MonitoredBy-2\#ChannelRegularConversion=__NULL
ADC1.MonitoredBy-3\#ChannelRegularConversion=__NULL
ADC1.NbrOfConversion=3
ADC1.NbrOfConversionFlag=1
ADC1.OffsetNumber-1\#ChannelRegularConversion=ADC_OFFSET_NONE
ADC1.OffsetNumber-2\#ChannelRegularConversion=ADC_OFFSET_NONE
ADC1.OffsetNumber-3\#ChannelRegularConversion=ADC_OFFSET_NONE
ADC1.Rank-1\#ChannelRegularConversion=1
ADC1.Rank-2\#ChannelRegularConversion=2
ADC1.Rank-3\#ChannelRegularConversion=3
ADC1.SamplingTime-1\#ChannelRegularConversion=ADC_SAMPLETIME_814CYCLES
ADC1.SamplingTime-2\#ChannelRegularConversion=ADC_SAMPLETIME_20CYCLES
ADC1.SamplingTime-3\#ChannelRegularConversion=ADC_SAMPLETIME_20CYCLES
ADC1.master=1
CAD.formats=
CAD.pinconfig=
CAD.provider=
CORTEX_M33_NS.userName=CORTEX_M33
File.Version=6
GPDMA1.CIRCULARMODE_GPDMACH0=DISABLE
GPDMA1.DESTDATAWIDTH_GPDMACH0=DMA_DEST_DATAWIDTH_HALFWORD
GPDMA1.DESTINC_GPDMACH0=DMA_DINC_INCREMENTED
GPDMA1.DESTINC_GPDMACH1=DMA_DINC_INCREMENTED
GPDMA1.DESTINC_GPDMACH3=DMA_DINC_INCREMENTED
GPDMA1.DIRECTION_GPDMACH2=DMA_MEMORY_TO_PERIPH
GPDMA1.DIRECTION_GPDMACH4=DMA_MEMORY_TO_PERIPH
GPDMA1.IPHANDLE_GPDMACH0-SIMPLEREQUEST_GPDMACH0=__NULL
GPDMA1.IPHANDLE_GPDMACH1-SIMPLEREQUEST_GPDMACH1=__NULL
GPDMA1.IPHANDLE_GPDMACH2-SIMPLEREQUEST_GPDMACH2=__NULL
GPDMA1.IPHANDLE_GPDMACH3-SIMPLEREQUEST_GPDMACH3=__NULL
GPDMA1.IPHANDLE_GPDMACH4-SIMPLEREQUEST_GPDMACH4=__NULL
GPDMA1.IPParameters=REQUEST_GPDMACH0,CIRCULARMODE_GPDMACH0,DESTDATAWIDTH_GPDMACH0,SRCDATAWIDTH_GPDMACH0,DESTINC_GPDMACH0,REQUEST_GPDMACH2,DIRECTION_GPDMACH2,SRCINC_GPDMACH2,REQUEST_GPDMACH3,DESTINC_GPDMACH3,IPHANDLE_GPDMACH3-SIMPLEREQUEST_GPDMACH3,IPHANDLE_GPDMACH2-SIMPLEREQUEST_GPDMACH2,IPHANDLE_GPDMACH0-SIMPLEREQUEST_GPDMACH0,IPHANDLE_GPDMACH1-SIMPLEREQUEST_GPDMACH1,REQUEST_GPDMACH1,IPHANDLE_GPDMACH4-SIMPLEREQUEST_GPDMACH4,REQUEST_GPDMACH4,DIRECTION_GPDMACH4,SRCINC_GPDMACH4,DESTINC_GPDMACH1
GPDMA1.REQUEST_GPDMACH0=GPDMA1_REQUEST_ADC1
GPDMA1.REQUEST_GPDMACH1=GPDMA1_REQUEST_SPI1_RX
GPDMA1.REQUEST_GPDMACH2=GPDMA1_REQUEST_SPI3_TX
GPDMA1.REQUEST_GPDMACH3=GPDMA1_REQUEST_SPI3_RX
GPDMA1.REQUEST_GPDMACH4=GPDMA1_REQUEST_SPI1_TX
GPDMA1.SRCDATAWIDTH_GPDMACH0=DMA_SRC_DATAWIDTH_HALFWORD
GPDMA1.SRCINC_GPDMACH2=DMA_SINC_INCREMENTED
GPDMA1.SRCINC_GPDMACH4=DMA_SINC_INCREMENTED
GPIO.groupedBy=Group By Peripherals
KeepUserPlacement=false
MMTAppRegionsCount=0
MMTConfigApplied=false
MMTSectionSuffix=
Mcu.CPN=STM32U595RJT6Q
Mcu.ContextProject=TrustZoneDisabled
Mcu.Family=STM32U5
Mcu.IP0=ADC1
Mcu.IP1=CORTEX_M33_NS
Mcu.IP10=NVIC
Mcu.IP11=PWR
Mcu.IP12=RCC
Mcu.IP13=SPI1
Mcu.IP14=SPI3
Mcu.IP15=SYS
Mcu.IP16=TIM2
Mcu.IP17=USB_OTG_HS
Mcu.IP2=CRC
Mcu.IP3=DEBUG
Mcu.IP4=FLASH
Mcu.IP5=GPDMA1
Mcu.IP6=ICACHE
Mcu.IP7=LPBAM
Mcu.IP8=LPBAMQUEUE
Mcu.IP9=MEMORYMAP
Mcu.IPNb=18
Mcu.Name=STM32U595RJTxQ
Mcu.Package=LQFP64
Mcu.Pin0=PC14-OSC32_IN (PC14)
Mcu.Pin1=PC15-OSC32_OUT (PC15)
Mcu.Pin10=PA7
Mcu.Pin11=PB0
Mcu.Pin12=PB1
Mcu.Pin13=PC8
Mcu.Pin14=PC9
Mcu.Pin15=PA8
Mcu.Pin16=PA11
Mcu.Pin17=PA12
Mcu.Pin18=PA13 (JTMS/SWDIO)
Mcu.Pin19=PA14 (JTCK/SWCLK)
Mcu.Pin2=PH0-OSC_IN (PH0)
Mcu.Pin20=PC10
Mcu.Pin21=PC11
Mcu.Pin22=PC12
Mcu.Pin23=PD2
Mcu.Pin24=PB3 (JTDO/TRACESWO)
Mcu.Pin25=PB4 (NJTRST)
Mcu.Pin26=PB5
Mcu.Pin27=PB6
Mcu.Pin28=VP_CRC_VS_CRC
Mcu.Pin29=VP_FLASH_SIG_Activate_FlashIP
Mcu.Pin3=PH1-OSC_OUT (PH1)
Mcu.Pin30=VP_GPDMA1_VS_GPDMACH0
Mcu.Pin31=VP_GPDMA1_VS_GPDMACH1
Mcu.Pin32=VP_GPDMA1_VS_GPDMACH2
Mcu.Pin33=VP_GPDMA1_VS_GPDMACH3
Mcu.Pin34=VP_GPDMA1_VS_GPDMACH4
Mcu.Pin35=VP_ICACHE_VS_ICACHE
Mcu.Pin36=VP_LPBAMQUEUE_VS_QUEUE
Mcu.Pin37=VP_PWR_VS_SECSignals
Mcu.Pin38=VP_PWR_VS_LPOM
Mcu.Pin39=VP_PWR_Vdda
Mcu.Pin4=PA0
Mcu.Pin40=VP_SYS_VS_Systick
Mcu.Pin41=VP_TIM2_VS_ClockSourceINT
Mcu.Pin42=VP_LPBAM_VS_SIG1
Mcu.Pin43=VP_LPBAM_VS_SIG4
Mcu.Pin44=VP_MEMORYMAP_VS_MEMORYMAP
Mcu.Pin5=PA1
Mcu.Pin6=PA2
Mcu.Pin7=PA3
Mcu.Pin8=PA5
Mcu.Pin9=PA6
Mcu.PinsNb=45
Mcu.ThirdPartyNb=0
Mcu.UserConstants=
Mcu.UserName=STM32U595RJTxQ
MxCube.Version=6.17.0
MxDb.Version=DB.6.0.170
NVIC.BusFault_IRQn=true\:0\:0\:false\:false\:true\:false\:false\:false
NVIC.DebugMonitor_IRQn=true\:0\:0\:false\:false\:true\:false\:false\:false
NVIC.EXTI0_IRQn=true\:5\:0\:true\:false\:true\:true\:true\:true
NVIC.EXTI1_IRQn=true\:5\:0\:true\:false\:true\:true\:true\:true
NVIC.ForceEnableDMAVector=true
NVIC.GPDMA1_Channel0_IRQn=true\:4\:0\:true\:false\:true\:true\:true\:true
NVIC.GPDMA1_Channel1_IRQn=true\:4\:0\:true\:false\:true\:true\:true\:true
NVIC.GPDMA1_Channel2_IRQn=true\:4\:0\:true\:false\:true\:false\:true\:true
NVIC.GPDMA1_Channel3_IRQn=true\:4\:0\:true\:false\:true\:false\:true\:true
NVIC.GPDMA1_Channel4_IRQn=true\:4\:0\:true\:false\:true\:false\:true\:true
NVIC.HardFault_IRQn=true\:0\:0\:false\:false\:true\:false\:false\:false
NVIC.MemoryManagement_IRQn=true\:0\:0\:false\:false\:true\:false\:false\:false
NVIC.NonMaskableInt_IRQn=true\:0\:0\:false\:false\:true\:false\:false\:false
NVIC.OTG_HS_IRQn=true\:6\:0\:true\:false\:true\:true\:true\:true
NVIC.PendSV_IRQn=true\:0\:0\:false\:false\:true\:false\:false\:false
NVIC.PriorityGroup=NVIC_PRIORITYGROUP_4
NVIC.SPI1_IRQn=true\:4\:0\:true\:false\:true\:false\:true\:true
NVIC.SPI3_IRQn=true\:4\:0\:true\:false\:true\:false\:true\:true
NVIC.SVCall_IRQn=true\:0\:0\:false\:false\:true\:false\:false\:false
NVIC.SysTick_IRQn=true\:0\:0\:true\:false\:true\:false\:true\:false
NVIC.UsageFault_IRQn=true\:0\:0\:false\:false\:true\:false\:false\:false
PA0.GPIOParameters=GPIO_Label
PA0.GPIO_Label=IMU_INT1
PA0.Locked=true
PA0.Signal=GPXTI0
PA1.GPIOParameters=GPIO_Label
PA1.GPIO_Label=IMU_INT2
PA1.Locked=true
PA1.Signal=GPXTI1
PA11.Mode=Internal_Phy_Device
PA11.Signal=USB_OTG_HS_DM
PA12.Mode=Internal_Phy_Device
PA12.Signal=USB_OTG_HS_DP
PA13\ (JTMS/SWDIO).Mode=Serial_Wire
PA13\ (JTMS/SWDIO).Signal=DEBUG_JTMS-SWDIO
PA14\ (JTCK/SWCLK).Mode=Serial_Wire
PA14\ (JTCK/SWCLK).Signal=DEBUG_JTCK-SWCLK
PA2.Mode=IN7-Single-Ended
PA2.Signal=ADC1_IN7
PA3.GPIOParameters=GPIO_Speed,PinState,GPIO_Label,GPIO_ModeDefaultOutputPP
PA3.GPIO_Label=IMU_CS
PA3.GPIO_ModeDefaultOutputPP=GPIO_MODE_OUTPUT_PP
PA3.GPIO_Speed=GPIO_SPEED_FREQ_LOW
PA3.Locked=true
PA3.PinState=GPIO_PIN_SET
PA3.Signal=GPIO_Output
PA5.Mode=Full_Duplex_Master
PA5.Signal=SPI1_SCK
PA6.GPIOParameters=GPIO_PuPd
PA6.GPIO_PuPd=GPIO_NOPULL
PA6.Mode=Full_Duplex_Master
PA6.Signal=SPI1_MISO
PA7.Mode=Full_Duplex_Master
PA7.Signal=SPI1_MOSI
PA8.GPIOParameters=PinState,GPIO_Label
PA8.GPIO_Label=ECG_SDN
PA8.Locked=true
PA8.PinState=GPIO_PIN_SET
PA8.Signal=GPIO_Output
PB0.Mode=IN15-Single-Ended
PB0.Signal=ADC1_IN15
PB1.Mode=IN16-Single-Ended
PB1.Signal=ADC1_IN16
PB3\ (JTDO/TRACESWO).GPIOParameters=GPIO_Label
PB3\ (JTDO/TRACESWO).GPIO_Label=LED_1
PB3\ (JTDO/TRACESWO).Locked=true
PB3\ (JTDO/TRACESWO).Signal=GPIO_Output
PB4\ (NJTRST).GPIOParameters=GPIO_Label
PB4\ (NJTRST).GPIO_Label=LED_2
PB4\ (NJTRST).Locked=true
PB4\ (NJTRST).Signal=GPIO_Output
PB5.GPIOParameters=GPIO_Label
PB5.GPIO_Label=LED_3
PB5.Locked=true
PB5.Signal=GPIO_Output
PB6.GPIOParameters=GPIO_Label
PB6.GPIO_Label=LED_4
PB6.Locked=true
PB6.Signal=GPIO_Output
PC10.Mode=Full_Duplex_Master
PC10.Signal=SPI3_SCK
PC11.Mode=Full_Duplex_Master
PC11.Signal=SPI3_MISO
PC12.Mode=Full_Duplex_Master
PC12.Signal=SPI3_MOSI
PC14-OSC32_IN\ (PC14).Mode=LSE-External-Oscillator
PC14-OSC32_IN\ (PC14).Signal=RCC_OSC32_IN
PC15-OSC32_OUT\ (PC15).Mode=LSE-External-Oscillator
PC15-OSC32_OUT\ (PC15).Signal=RCC_OSC32_OUT
PC8.GPIOParameters=GPIO_Label
PC8.GPIO_Label=ECG_LOP
PC8.Locked=true
PC8.Signal=GPIO_Input
PC9.GPIOParameters=GPIO_Label
PC9.GPIO_Label=ECG_LON
PC9.Locked=true
PC9.Signal=GPIO_Input
PD2.GPIOParameters=GPIO_Speed,PinState,GPIO_Label
PD2.GPIO_Label=Flash_CS
PD2.GPIO_Speed=GPIO_SPEED_FREQ_VERY_HIGH
PD2.Locked=true
PD2.PinState=GPIO_PIN_SET
PD2.Signal=GPIO_Output
PH0-OSC_IN\ (PH0).Mode=HSE-External-Oscillator
PH0-OSC_IN\ (PH0).Signal=RCC_OSC_IN
PH1-OSC_OUT\ (PH1).Mode=HSE-External-Oscillator
PH1-OSC_OUT\ (PH1).Signal=RCC_OSC_OUT
PWR.IPParameters=PowerMode
PWR.PowerMode=PWR_SMPS_SUPPLY
PinOutPanel.RotationAngle=0
ProjectManager.AskForMigrate=true
ProjectManager.BackupPrevious=false
ProjectManager.CompilerLinker=GCC
ProjectManager.CompilerOptimize=6
ProjectManager.ComputerToolchain=false
ProjectManager.CoupleFile=false
ProjectManager.CustomerFirmwarePackage=
ProjectManager.DefaultFWLocation=true
ProjectManager.DeletePrevious=true
ProjectManager.DeviceId=STM32U595RJTxQ
ProjectManager.FirmwarePackage=STM32Cube FW_U5 V1.8.0
ProjectManager.FreePins=false
ProjectManager.FreePinsContext=
ProjectManager.HalAssertFull=false
ProjectManager.HeapSize=0x2000
ProjectManager.KeepUserCode=true
ProjectManager.LPBAM.generateCode=
ProjectManager.LastFirmware=true
ProjectManager.LibraryCopy=1
ProjectManager.MainLocation=Core/Src
ProjectManager.NoMain=false
ProjectManager.PreviousToolchain=STM32CubeIDE
ProjectManager.ProjectBuild=false
ProjectManager.ProjectFileName=fw.ioc
ProjectManager.ProjectName=fw
ProjectManager.ProjectStructure=
ProjectManager.RegisterCallBack=
ProjectManager.StackSize=0x4000
ProjectManager.TargetToolchain=STM32CubeIDE
ProjectManager.ToolChainLocation=
ProjectManager.UAScriptAfterPath=
ProjectManager.UAScriptBeforePath=
ProjectManager.UnderRoot=true
ProjectManager.functionlistsort=1-SystemClock_Config-RCC-false-HAL-false,2-MX_GPIO_Init-GPIO-false-HAL-true,3-MX_GPDMA1_Init-GPDMA1-false-HAL-true,4-MX_ADC1_Init-ADC1-false-HAL-true,5-MX_CRC_Init-CRC-false-HAL-true,6-MX_FLASH_Init-FLASH-false-HAL-true,7-MX_ICACHE_Init-ICACHE-false-HAL-true,8-MX_SPI3_Init-SPI3-false-HAL-true,9-MX_USB_OTG_HS_PCD_Init-USB_OTG_HS-false-HAL-true,10-MX_SPI1_Init-SPI1-false-HAL-true,11-MX_TIM2_Init-TIM2-false-HAL-true,0-MX_CORTEX_M33_NS_Init-CORTEX_M33_NS-false-HAL-true,0-MX_PWR_Init-PWR-false-HAL-true
RCC.ADCCLockSelection=RCC_ADCDACCLKSOURCE_HSE
RCC.ADCFreq_Value=16000000
RCC.ADF1Freq_Value=160000000
RCC.AHBFreq_Value=160000000
RCC.APB1CLKDivider=RCC_HCLK_DIV2
RCC.APB1Freq_Value=80000000
RCC.APB1TimFreq_Value=160000000
RCC.APB2CLKDivider=RCC_HCLK_DIV2
RCC.APB2Freq_Value=80000000
RCC.APB2TimFreq_Value=160000000
RCC.APB3CLKDivider=RCC_HCLK_DIV2
RCC.APB3Freq_Value=80000000
RCC.CK48Freq_Value=48000000
RCC.CRSFreq_Value=48000000
RCC.CortexFreq_Value=160000000
RCC.DACFreq_Value=32000
RCC.EPOD_VALUE=16000000
RCC.FCLKCortexFreq_Value=160000000
RCC.FDCANFreq_Value=160000000
RCC.FamilyName=M
RCC.HCLKFreq_Value=160000000
RCC.HSE_VALUE=16000000
RCC.HSI48_VALUE=48000000
RCC.HSI_VALUE=16000000
RCC.I2C1Freq_Value=80000000
RCC.I2C2Freq_Value=80000000
RCC.I2C3Freq_Value=80000000
RCC.I2C4Freq_Value=80000000
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

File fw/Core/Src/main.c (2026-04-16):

/* USER CODE BEGIN Header */
/**
  ******************************************************************************
  * @file           : main.c
  * @brief          : Main program body
  ******************************************************************************
  * @attention
  *
  * Copyright (c) 2026 STMicroelectronics.
  * All rights reserved.
  *
  * This software is licensed under terms that can be found in the LICENSE file
  * in the root directory of this software component.
  * If no LICENSE file comes with this software, it is provided AS-IS.
  *
  ******************************************************************************
  */
/* USER CODE END Header */
/* Includes ------------------------------------------------------------------*/
#include "main.h"

/* Private includes ----------------------------------------------------------*/
/* USER CODE BEGIN Includes */
#include <string.h>

#include "tusb.h"
#include "usb_cdc.h"

#include "st1vafe6ax.h"
#include "data_types.h"
#include "ecg_dsp.h"
#include "imu_dsp.h"
/* USER CODE END Includes */

/* Private typedef -----------------------------------------------------------*/
/* USER CODE BEGIN PTD */

/* USER CODE END PTD */

/* Private define ------------------------------------------------------------*/
/* USER CODE BEGIN PD */

/* Telemetry */
#define TELEMETRY_HEADER    0xAABBU
#define EVENT_HEADER        0xCCDDU
#define BREATH_HEADER       0xEEFFU
#define HRV_HEADER          0xFFAAU

/* FIFO sizes must be powers of 2 */
#define SENSOR_FIFO_SIZE    1024U
#define TELEMETRY_FIFO_SIZE 512U

/* USER CODE END PD */

/* Private macro -------------------------------------------------------------*/
/* USER CODE BEGIN PM */

/* USER CODE END PM */

/* Private variables ---------------------------------------------------------*/
ADC_HandleTypeDef hadc1;
DMA_HandleTypeDef handle_GPDMA1_Channel0;

CRC_HandleTypeDef hcrc;

SPI_HandleTypeDef hspi1;
SPI_HandleTypeDef hspi3;
DMA_HandleTypeDef handle_GPDMA1_Channel4;
DMA_HandleTypeDef handle_GPDMA1_Channel1;
DMA_HandleTypeDef handle_GPDMA1_Channel3;
DMA_HandleTypeDef handle_GPDMA1_Channel2;

TIM_HandleTypeDef htim2;

PCD_HandleTypeDef hpcd_USB_OTG_HS;

/* USER CODE BEGIN PV */

/*
 * SPI TX buffer for reading 12 bytes of gyroscope + accelerometer output.
 *
 * The first byte is the register address with the read bit set.
 * Bytes 1-12 are dummies clocked out while the IMU shifts data back.
 * Starting at OUTX_L_G (0x22), registers are contiguous through 0x2D:
 *   0x22..0x27: Gyro  X_L, X_H, Y_L, Y_H, Z_L, Z_H
 *   0x28..0x2D: Accel Z_L, Z_H, Y_L, Y_H, X_L, X_H
 */
static uint8_t imu_tx[13] =
  { ST1VAFE6AX_REG_OUTX_L_G | ST1VAFE6AX_READ_BIT,
    0, 0, 0, 0, 0, 0, 0, 0, 0, 0, 0, 0 };

volatile uint8_t system_ready = 0;

DataSample_t sensor_fifo[SENSOR_FIFO_SIZE];
volatile uint16_t sensor_fifo_head = 0;
volatile uint16_t sensor_fifo_tail = 0;

TelemetryPacket_t telemetry_fifo[TELEMETRY_FIFO_SIZE];
uint16_t telemetry_fifo_head = 0;
uint16_t telemetry_fifo_tail = 0;

volatile uint8_t spi_finished = 0;
volatile uint8_t adc_finished = 0;
volatile uint8_t dma_in_progress = 0;
/* USER CODE END PV */
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

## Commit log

2025-12-23 Collector Rev1 design
    [HM-Collector-Rev1.kicad_pcb, HM-Collector-Rev1.kicad_sch]
2026-03-01 Rev2 design files
    [BOM-HM-Collector-Rev2.csv, CPL-HM-Collector-Rev2.csv, HM-Collector-Rev2-CuBottom.gbr, HM-Collector-Rev2-CuIn1.gbr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]
2026-03-01 Fix image path in README.md
    Updated image path for the Health Monitor PCB.
2026-03-07 Rename Rev1 directory and add documentation/production files
    [HM-Rev1.kicad_pcb, HM-Rev1.kicad_sch, bom.csv, designators.csv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]
2026-04-16 Increase sensor FIFO size
